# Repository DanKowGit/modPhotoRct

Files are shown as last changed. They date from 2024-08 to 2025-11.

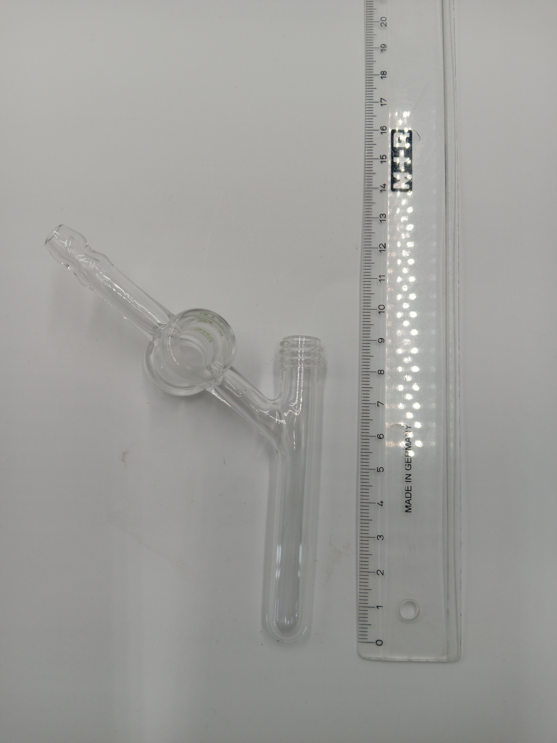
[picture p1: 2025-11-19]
01_CAD/00_Corpus/03_Corpus_130x130x130mm_water_splitting_group_power_measurment/05_reactors/GL14 5 mL schlenk flask.jpg

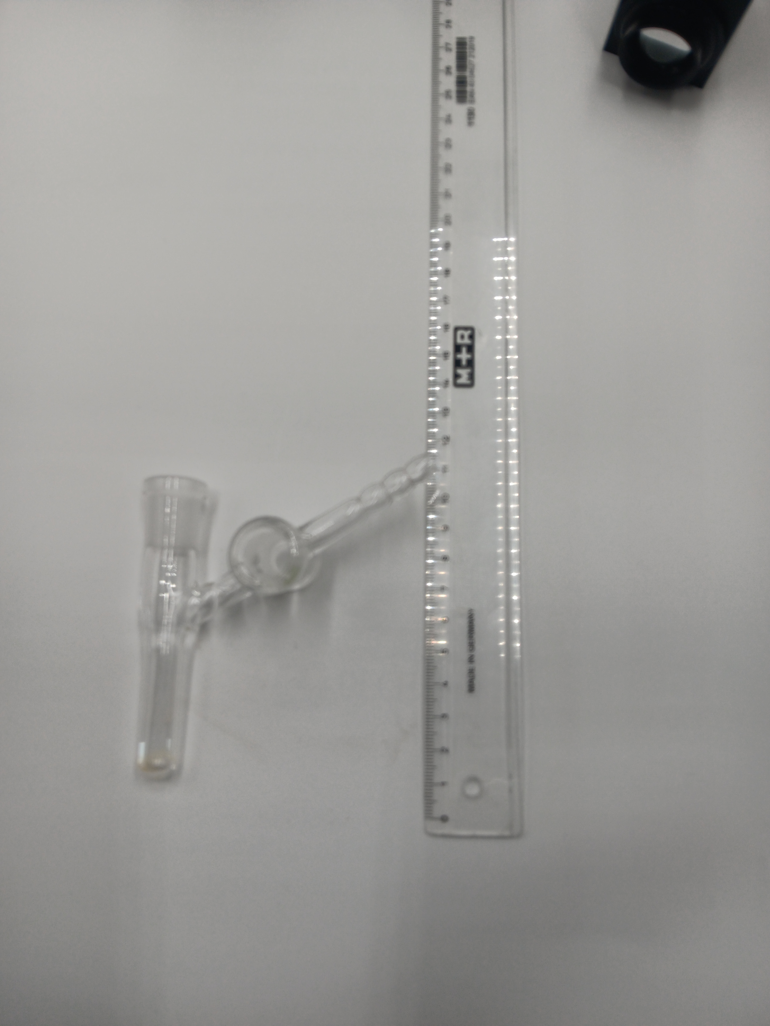
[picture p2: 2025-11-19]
01_CAD/00_Corpus/03_Corpus_130x130x130mm_water_splitting_group_power_measurment/05_reactors/NS14 5 mL schlenk flask.jpg

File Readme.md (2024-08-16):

# modularPhotoreactor

A modular and characterized open source photoreactor and the mutli-batch screening phototreactor extension

## Documentation

The assembly of the devices is documented in the [CAD section](./01_CAD/).

See also the 3D-pdfs for detailed assembly instructions in the [assembly section](./03_ASSEMBLY_INSTRUCTIONS/).

The Python modules for the operation of the reactor controller are documented in the repository [Py4ModPhotoreactor](https://github.com/photonZfeed/Py4ModPhotoreactor). See also the fairly detailed docstrings in the code. 

## Folder Structure

```
📦modPhotoRct
┣ 📂01_CAD
┃   ┣ 📂00_Corpus
┃   ┃   ┣ 📂00_Corpus_90x90x100mm
┃   ┃   ┃   ┣ 📂00_corpus
┃   ┃   ┃   ┃   ┣ 📜corpus_90x90x100mm_back_wall.stl
┃   ┃   ┃   ┃   ┣ 📜corpus_90x90x100mm_front_wall.stl
┃   ┃   ┃   ┃   ┣ 📜corpus_90x90x100mm_side_walls.stl
┃   ┃   ┃   ┃   ┣ 📜corpus_90x90x100mm_side_walls_LED_holder.stl
┃   ┃   ┃   ┃   ┣ 📜corpus_cover.stl
┃   ┃   ┃   ┃   ┗ 📜corpus_stand.stl
┃   ┃   ┃   ┣ 📂01_irradiation_module
┃   ┃   ┃   ┃   ┣ 📜20210104_Thorlabsl_modul.stl
┃   ┃   ┃   ┃   ┣ 📜corpus_90x90mm_irrad_Max350.stl
┃   ┃   ┃   ┃   ┣ 📜corpus_90x90mm_irrad_Max350_adapter.stl
┃   ┃   ┃   ┃   ┣ 📜corpus_90x90mm_irrad_Thorlabs.stl
┃   ┃   ┃   ┃   ┣ 📜corpus_90x90mm_irrad_Thorlabs_adapter.stl
┃   ┃   ┃   ┃   ┣ 📜corpus_90x90mm_irrad_Thorlabs_collimator.stl
┃   ┃   ┃   ┃   ┗ 📜corpus_90x90mm_irrad_starcool.stl
┃   ┃   ┃   ┣ 📂02_stirring_module
┃   ┃   ┃   ┃   ┣ 📜corpus_90x90mm_stirring_module.stl
┃   ┃   ┃   ┃   ┣ 📜corpus_90x90mm_stirring_module_holder_electric_motor.stl
┃   ┃   ┃   ┃   ┣ 📜corpus_90x90mm_stirring_module_magnet_holder.stl
┃   ┃   ┃   ┃   ┗ 📜corpus_90x90mm_stirring_module_magnet_holder_blind_plug.stl
┃   ┃   ┃   ┗ 📂03_sample_holders
┃   ┃   ┃   ┃   ┣ 📜corpus_90x90mm_4mL_GCvial_ND13_10S_alignment_holder.stl
┃   ┃   ┃   ┃   ┣ 📜corpus_90x90mm_4mL_GCvial_ND13_10S_holder.stl
┃   ┃   ┃   ┃   ┣ 📜corpus_90x90mm_4mL_GCvial_ND13_1S_alignment_holder.stl
┃   ┃   ┃   ┃   ┣ 📜corpus_90x90mm_4mL_GCvial_ND13_1S_holder.stl
┃   ┃   ┃   ┃   ┣ 📜corpus_90x90mm_4mL_GCvial_ND13_4S_alignment_holder.stl
┃   ┃   ┃   ┃   ┣ 📜corpus_90x90mm_4mL_GCvial_ND13_4S_holder.stl
┃   ┃   ┃   ┃   ┣ 📜corpus_90x90mm_4mL_GCvial_ND13_6S_alignment_holder.stl
┃   ┃   ┃   ┃   ┣ 📜corpus_90x90mm_4mL_GCvial_ND13_6S_holder.stl
┃   ┃   ┃   ┃   ┣ 📜corpus_90x90mm_4mL_GCvial_ND13_8S_alignment_holder.stl
┃   ┃   ┃   ┃   ┣ 📜corpus_90x90mm_4mL_GCvial_ND13_8S_holder.stl
┃   ┃   ┃   ┃   ┣ 📜corpus_90x90mm_8mL_GCvial_ND13_10S_alignment_holder.stl
┃   ┃   ┃   ┃   ┗ 📜corpus_90x90mm_8mL_GCvial_ND13_1S_alignment_holder.stl
┃   ┃   ┣ 📂01_Corpus_90x90x140mm
┃   ┃   ┃   ┣ 📂00_corpus
┃   ┃   ┃   ┃   ┣ 📜corpus_90x90x140mm_back_wall.stl
┃   ┃   ┃   ┃   ┣ 📜corpus_90x90x140mm_front_wall.stl
┃   ┃   ┃   ┃   ┣ 📜corpus_90x90x140mm_side_walls.stl
┃   ┃   ┃   ┃   ┣ 📜corpus_90x90x140mm_side_walls_LED_Irradiation_Firesting_ports.ipt
┃   ┃   ┃   ┃   ┣ 📜corpus_90x90x140mm_side_walls_LED_Irradiation_Firesting_ports.stl
┃   ┃   ┃   ┃   ┣ 📜corpus_90x90x140mm_side_walls_LED_Irradiation_Firesting_ports.yaml
┃   ┃   ┃   ┃   ┣ 📜corpus_cover.stl
┃   ┃   ┃   ┃   ┗ 📜corpus_stand.stl
┃   ┃   ┃   ┣ 📂01_irradiation_module
┃   ┃   ┃   ┃   ┣ 📜20210104_Thorlabsl_modul.stl
┃   ┃   ┃   ┃   ┣ 📜corpus_90x90mm_irrad_Max350.stl
┃   ┃   ┃   ┃   ┣ 📜corpus_90x90mm_irrad_Max350_adapter.stl
┃   ┃   ┃   ┃   ┣ 📜corpus_90x90mm_irrad_Thorlabs.stl
┃   ┃   ┃   ┃   ┣ 📜corpus_90x90mm_irrad_Thorlabs_adapter.stl
┃   ┃   ┃   ┃   ┣ 📜corpus_90x90mm_irrad_Thorlabs_collimator.stl
┃   ┃   ┃   ┃   ┗ 📜corpus_90x90mm_irrad_starcool.stl
┃   ┃   ┃   ┣ 📂02_stirring_module
┃   ┃   ┃   ┃   ┣ 📜corpus_90x90mm_stirring_module.stl
┃   ┃   ┃   ┃   ┣ 📜corpus_90x90mm_stirring_module_holder_electric_motor.stl
┃   ┃   ┃   ┃   ┣ 📜corpus_90x90mm_stirring_module_magnet_holder.stl
┃   ┃   ┃   ┃   ┗ 📜corpus_90x90mm_stirring_module_magnet_holder_blind_plug.stl
┃   ┃   ┃   ┗ 📂03_sample_holders
┃   ┃   ┃   ┃   ┣ 📜corpus_90x90mm_4mL_GCvial_ND13_10S_alignment_holder.stl
┃   ┃   ┃   ┃   ┣ 📜corpus_90x90mm_4mL_GCvial_ND13_10S_holder.stl
┃   ┃   ┃   ┃   ┣ 📜corpus_90x90mm_4mL_GCvial_ND13_1S_alignment_holder.stl
┃   ┃   ┃   ┃   ┣ 📜corpus_90x90mm_4mL_GCvial_ND13_1S_holder.stl
┃   ┃   ┃   ┃   ┣ 📜corpus_90x90mm_4mL_GCvial_ND13_4S_alignment_holder.stl
┃   ┃   ┃   ┃   ┣ 📜corpus_90x90mm_4mL_GCvial_ND13_4S_holder.stl
┃   ┃   ┃   ┃   ┣ 📜corpus_90x90mm_4mL_GCvial_ND13_6S_alignment_holder.stl
┃   ┃   ┃   ┃   ┣ 📜corpus_90x90mm_4mL_GCvial_ND13_6S_holder.stl
┃   ┃   ┃   ┃   ┣ 📜corpus_90x90mm_4mL_GCvial_ND13_8S_alignment_holder.stl
┃   ┃   ┃   ┃   ┣ 📜corpus_90x90mm_4mL_GCvial_ND13_8S_holder.stl
┃   ┃   ┃   ┃   ┣ 📜corpus_90x90mm_8mL_GCvial_ND13_10S_alignment_holder.stl
┃   ┃   ┃   ┃   ┗ 📜corpus_90x90mm_8mL_GCvial_ND13_1S_alignment_holder.stl
┃   ┃   ┗ 📂02_Corpus_130x130x130mm
┃   ┃   ┃   ┣ 📂00_corpus
┃   ┃   ┃   ┃   ┣ 📜corpus130x130mm_side_walls.stl
┃   ┃   ┃   ┃   ┣ 📜corpus_130x130mm_back_wall.stl
┃   ┃   ┃   ┃   ┣ 📜corpus_130x130mm_cover.stl
┃   ┃   ┃   ┃   ┣ 📜corpus_130x130mm_front_wall_monting_thermal_hose.stl
┃   ┃   ┃   ┃   ┣ 📜corpus_130x130mm_side_wall_left.stl
┃   ┃   ┃   ┃   ┣ 📜corpus_130x130mm_side_wall_right.stl
┃   ┃   ┃   ┃   ┣ 📜corpus_130x130mm_stand_20mm.stl
┃   ┃   ┃   ┃   ┣ 📜fin_back_wall.stl
┃   ┃   ┃   ┃   ┣ 📜fin_front_wall.stl
┃   ┃   ┃   ┃   ┣ 📜spacer_side_walls_5mm.stl
┃   ┃   ┃   ┃   ┗ 📜spacer_stand_5mm.stl
┃   ┃   ┃   ┣ 📂01_irradiation_module
┃   ┃   ┃   ┃   ┗ 📜irrad_module.stl
┃   ┃   ┃   ┣ 📂02_sample_holders
┃   ┃   ┃   ┃   ┣ 📜corpus_130x130mm_GCvial_ND13_18S_alignment_holder.stl
┃   ┃   ┃   ┃   ┣ 📜corpus_130x130mm_GCvial_ND13_18S_holder.stl
┃   ┃   ┃   ┃   ┣ 📜corpus_130x130mm_GCvial_ND13_1S_alignment_holder.stl
┃   ┃   ┃   ┃   ┗ 📜corpus_130x130mm_GCvial_ND13_1S_holder.stl
┃   ┃   ┃   ┗ 📂03_tempering_module
┃   ┃   ┃   ┃   ┣ 📜back_mounting_thermo_hose.stl
┃   ┃   ┃   ┃   ┣ 📜fan_holder.stl
┃   ┃   ┃   ┃   ┣ 📜holder_tempering_module.stl
┃   ┃   ┃   ┃   ┣ 📜mounting_alu_water_cooler.stl
┃   ┃   ┃   ┃   ┗ 📜spacer_holder_tempering_module.stl
┃   ┣ 📂01_controller
┃   ┃   ┣ 📜controller_case.stl
┃   ┃   ┣ 📜controller_case_LCD_holder.stl
┃   ┃   ┗ 📜controller_electronic_board_holder.stl
┃   ┣ 📂02_Peripheral_Modules
┃   ┃   ┣ 📂00_ambient_temperature
┃   ┃   ┃   ┣ 📜base_plate_ambient_temperature_extension.stl
┃   ┃   ┃   ┗ 📜case_ambient_temperature_extension.stl
┃   ┃   ┣ 📂01_tempering_extension
┃   ┃   ┃   ┣ 📜base_plate.stl
┃   ┃   ┃   ┗ 📜case_tempering_extension.stl
┃   ┃   ┣ 📂02_master_extension
┃   ┃   ┃   ┣ 📜base_plate.stl
┃   ┃   ┃   ┗ 📜case_master_extension.stl
┃   ┃   ┣ 📂03_membrane_pump_extension
┃   ┃   ┃   ┣ 📜base_plate_membrane_pump.stl
┃   ┃   ┃   ┣ 📜base_plate_membrane_pump_exension.stl
┃   ┃   ┃   ┣ 📜case_membrane_pump.stl
┃   ┃   ┃   ┗ 📜case_membrane_pump_extension.stl
┃   ┃   ┗ 📂04_pressure_sensor_extension
┃   ┃   ┃   ┣ 📜base_plate.stl
┃   ┃   ┃   ┣ 📜base_plate_updated.stl
┃   ┃   ┃   ┣ 📜case_pressure_extension.stl
┃   ┃   ┃   ┗ 📜case_pressure_extension_updated.stl
┃   ┗ 📂03_Multi_Batch_Screening_Photoreactor
┃   ┃   ┣ 📂00_Base_Module
┃   ┃   ┃   ┗ 📜Base_Module.stl
┃   ┃   ┣ 📂01_Irradiation_Module
┃   ┃   ┃   ┣ 📜300mm_alu_heatsink.stl
┃   ┃   ┃   ┣ 📜heatsink_holder_left.stl
┃   ┃   ┃   ┣ 📜heatsink_holder_right.stl
┃   ┃   ┃   ┗ 📜stand_irradiation_module.stl
┃   ┃   ┣ 📂02_Reflector_Module
┃   ┃   ┃   ┣ 📜PTFE_Side_Wall.stl
┃   ┃   ┃   ┣ 📜Reflector_Holder_Nut.stl
┃   ┃   ┃   ┗ 📜Reflector_Holder_Screw.stl
┃   ┃   ┣ 📂03_Mobile_Cover
┃   ┃   ┃   ┣ 📜back.stl
┃   ┃   ┃   ┣ 📜connector.stl
┃   ┃   ┃   ┣ 📜front.stl
┃   ┃   ┃   ┣ 📜sides.stl
┃   ┃   ┃   ┗ 📜top.stl
┃   ┃   ┗ 📂04_Accesories
┃   ┃   ┃   ┗ 📂00_UV_Vis_Cell_4mL_GC_Vial
┃   ┃   ┃   ┃   ┣ 📜UV_vis_cell_4mL_GC_vial_SLA.png
┃   ┃   ┃   ┃   ┗ 📜UV_vis_cell_4mL_GC_vial_SLA.stl
┣ 📂02_MATERIALS
┃   ┣ 📂00_electronics
┃   ┃   ┣ 📂00_Tinkerforge
┃   ┃   ┃   ┗ 📜Tinkerforge.txt
┃   ┃   ┣ 📂01_LEDs
┃   ┃   ┃   ┣ 📂RGBA
┃   ┃   ┃   ┃   ┗ 📜LZ4-20MA00-0000.txt
┃   ┃   ┃   ┣ 📂UV
┃   ┃   ┃   ┃   ┣ 📂365nm
┃   ┃   ┃   ┃   ┃   ┗ 📜LST1-01G01-UV01-00.txt
┃   ┃   ┃   ┃   ┣ 📂385nm
┃   ┃   ┃   ┃   ┃   ┗ 📜LZ1-10UB00-01U4.txt
┃   ┃   ┃   ┃   ┗ 📂405nm
┃   ┃   ┃   ┃   ┃   ┣ 📂onecore
┃   ┃   ┃   ┃   ┃   ┃   ┗ 📜LZ1-10UB00-01U7.txt
┃   ┃   ┃   ┃   ┃   ┗ 📂quadcore
┃   ┃   ┃   ┃   ┃   ┃   ┗ 📜LZ4-V0UB0R-00U8.txt
┃   ┃   ┃   ┣ 📂blue
┃   ┃   ┃   ┃   ┣ 📂453nm
┃   ┃   ┃   ┃   ┃   ┗ 📜LZ4-00B208-0000.txt
┃   ┃   ┃   ┃   ┣ 📂455nm
┃   ┃   ┃   ┃   ┃   ┗ 📜LST1-01F06-RYL1-00.txt
┃   ┃   ┃   ┃   ┗ 📂460nm
┃   ┃   ┃   ┃   ┃   ┣ 📜5412869-LED_2520Engin_Datasheet_LuxiGen_LZ1-00DB00-1532005.pdf
┃   ┃   ┃   ┃   ┃   ┗ 📜LZ1-00DB00.txt
┃   ┃   ┃   ┗ 📂green
┃   ┃   ┃   ┃   ┗ 📂530nm
┃   ┃   ┃   ┃   ┃   ┗ 📜LST1-01F06-GRN1-00.txt
┃   ┃   ┣ 📂02_raspberry_pi
┃   ┃   ┃   ┗ 📜raspberry_pi_4_8GB.txt
┃   ┃   ┣ 📂03_sd_card
┃   ┃   ┃   ┗ 📜SD_card.txt
┃   ┃   ┣ 📂04_peltier_element
┃   ┃   ┃   ┗ 📜peltier.txt
┃   ┃   ┣ 📂05_power_supplies
┃   ┃   ┃   ┣ 📂00_12V_5A
┃   ┃   ┃   ┃   ┗ 📜12V_5A.txt
┃   ┃   ┃   ┣ 📂01_24V_6A
┃   ┃   ┃   ┃   ┗ 📜24V_6A.txt
┃   ┃   ┃   ┗ 📂02_Analoge_ACDC_Laboratory_Power_Supply
┃   ┃   ┃   ┃   ┗ 📜KORAD_KA3005P.txt
┃   ┃   ┣ 📂06_small_parts
┃   ┃   ┃   ┣ 📂00_stripboard
┃   ┃   ┃   ┃   ┗ 📜stripboard_WR_914-HP.txt
┃   ┃   ┃   ┣ 📂01_connection_jacks
┃   ┃   ┃   ┃   ┣ 📜2Pin_PCB_Mount_2.5mm_Pitch.txt
┃   ┃   ┃   ┃   ┣ 📜2Pin_PCB_Mount_5mm_Pitch.txt
┃   ┃   ┃   ┃   ┣ 📜Cable_extension_PWM_4-Pin_Moltex.txt
┃   ┃   ┃   ┃   ┣ 📜DC_Jack.txt
┃   ┃   ┃   ┃   ┣ 📜banana_plug_female.txt
┃   ┃   ┃   ┃   ┣ 📜banana_plug_male.txt
┃   ┃   ┃   ┃   ┗ 📜wago_2Conductur_clamp.txt
┃   ┃   ┃   ┣ 📂02_Stacking_Header_Raspberry_Pi
┃   ┃   ┃   ┃   ┗ 📜Stacking_Header_Raspberry_Pi.txt
┃   ┃   ┃   ┣ 📂03_two_position_switch
┃   ┃   ┃   ┃   ┗ 📜two_position_switch.txt
┃   ┃   ┃   ┗ 📂04_silicone_wire
┃   ┃   ┃   ┃   ┗ 📜silicone_wire.txt
┃   ┃   ┣ 📂07_LED_drivers
┃   ┃   ┃   ┣ 📜350mA_driver.txt
┃   ┃   ┃   ┣ 📜500mA_driver.txt
┃   ┃   ┃   ┗ 📜700mA_driver.txt
┃   ┃   ┣ 📂08_membrane_pump
┃   ┃   ┃   ┣ 📜Membrane_Pump.txt
┃   ┃   ┃   ┗ 📜accessories_membrane_pump.txt
┃   ┃   ┗ 📂09_fans
┃   ┃   ┃   ┣ 📂00_fan_corpus_90x90mm
┃   ┃   ┃   ┃   ┗ 📜fan.txt
┃   ┃   ┃   ┣ 📂01_fan_corpus_130x130mm
┃   ┃   ┃   ┃   ┣ 📜fan.txt
┃   ┃   ┃   ┃   ┗ 📜fan_update.txt
┃   ┃   ┃   ┣ 📂02_power_supply_fan_corpus_90x90mm
┃   ┃   ┃   ┃   ┗ 📜power_supply.txt
┃   ┃   ┃   ┗ 📂03_Pi_Fan
┃   ┃   ┃   ┃   ┗ 📜Pi_Fan.txt
┃   ┗ 📂01_accessories
┃   ┃   ┣ 📂00_thermal_tube
┃   ┃   ┃   ┗ 📜thermal_hose.txt
┃   ┃   ┣ 📂01_hose_clamps
┃   ┃   ┃   ┗ 📜hose_clamp.txt
┃   ┃   ┣ 📂02_screws_nuts
┃   ┃   ┃   ┣ 📂00_M3_Set
┃   ┃   ┃   ┃   ┗ 📜M3_screw_set.txt
┃   ┃   ┃   ┣ 📂01_Nylon_Spacer
┃   ┃   ┃   ┃   ┗ 📜nylon_spacer.txt
┃   ┃   ┃   ┗ 📂02_M3_60mm
┃   ┃   ┃   ┃   ┗ 📜M3_60mm.txt
┃   ┃   ┣ 📂03_cooler
┃   ┃   ┃   ┣ 📂00_tempering_module_cooler
┃   ┃   ┃   ┃   ┣ 📂00_pelltier_cooler
┃   ┃   ┃   ┃   ┃   ┗ 📜Alpine AM4 Passive.txt
┃   ┃   ┃   ┃   ┗ 📂01_alu_water_cooler
┃   ┃   ┃   ┃   ┃   ┗ 📜alu_water_cooler.txt
┃   ┃   ┃   ┗ 📂01_LED_cooler
┃   ┃   ┃   ┃   ┣ 📂00_25mm_cooler
┃   ┃   ┃   ┃   ┃   ┗ 📜sink_s-1265491.txt
┃   ┃   ┃   ┃   ┣ 📂01_50mm_cooler
┃   ┃   ┃   ┃   ┃   ┗ 📜sink_s-1265491.txt
┃   ┃   ┃   ┃   ┗ 📂02_300mm_cooler
┃   ┃   ┃   ┃   ┃   ┗ 📜ATS-EXL75-300-R0.txt
┃   ┃   ┣ 📂04_foam_rubber_seal
┃   ┃   ┃   ┗ 📜foam_rubber_seal.txt
┃   ┃   ┗ 📂05_PTFE
┃   ┃   ┃   ┣ 📂00_technical_PTFE
┃   ┃   ┃   ┃   ┗ 📜technical_PTFE.txt
┃   ┃   ┃   ┗ 📂01_optical_PTFE
┃   ┃   ┃   ┃   ┗ 📜optical_PTFE.txt
┣ 📂03_ASSEMBLY_INSTRUCTIONS
┃   ┣ 📂00_Corpus
┃   ┃   ┣ 📜Assembly_Photoreactor_Corpus_130x130x130mm.pdf
┃   ┃   ┣ 📜Assembly_Photoreactor_Corpus_90x90x140mm.pdf
┃   ┃   ┗ 📜Assembly_Photoreactor_Corpus_90x90x90mm.pdf
┃   ┣ 📂01_Controller
┃   ┃   ┣ 📜20211029_Stripboard_drill_holes.pdf
┃   ┃   ┣ 📜Controller_Documentation.pdf
┃   ┃   ┣ 📜Controller_circuit_diagram.pdf
┃   ┃   ┣ 📜Controller_circuit_diagram.svg
┃   ┃   ┣ 📜Logic_Controller.pdf
┃   ┃   ┣ 📜Logic_Controller.svg
┃   ┃   ┗ 📜Logic_Controller.vsdx
┃   ┣ 📂02_Peripheral_Modules
┃   ┃   ┣ 📂00_Tempering_Module
┃   ┃   ┃   ┣ 📜Peltier_Circuit_Diagram.pdf
┃   ┃   ┃   ┗ 📜Peltier_Circuit_Diagram.svg
┃   ┃   ┗ 📂01_LED_Driver_Module
┃   ┃   ┃   ┗ 📜LED Driver Module.pdf
┃   ┣ 📂03_Irradiation_Module
┃   ┃   ┗ 📜assembly_instruction_LED_cooler.pdf
┃   ┗ 📂04_Multi_Batch_Screening_Phororeactor
┃   ┃   ┣ 📂00_Photoreactor
┃   ┃   ┃   ┗ 📜Multi_Batch_Screening_Photoreactor_assembly.pdf
┃   ┃   ┗ 📂01_Mobile_Cover
┃   ┃   ┃   ┣ 📜Mobile_Cover_assembly.pdf
┃   ┃   ┃   ┗ 📜Mobile_Cover_assembly.stl
┣ 📂04_IMAGES
┃   ┣ 📜Licenses.png
┃   ┗ 📜Licenses.svg
┣ 📜License.md
┗ 📜Readme.md
```

## More Information

<!--- Cite this repository: [![DOI](https://zenodo.org/badge/368164449.svg)](https://zenodo.org/badge/latestdoi/368164449) --->

## Publications

* [Making Photocatalysis Comparable Using a Modular and Characterized Open-Source Photoreactor](https://chemistry-europe.onlinelibrary.wiley.com/doi/full/10.1002/cptc.202200044)

* [Making Photocatalysts Screenable - A Milli Scale Multi-Batch Screening Photoreactor as Extension for the Modular Photoreactor](https://fill_in_the_blank)

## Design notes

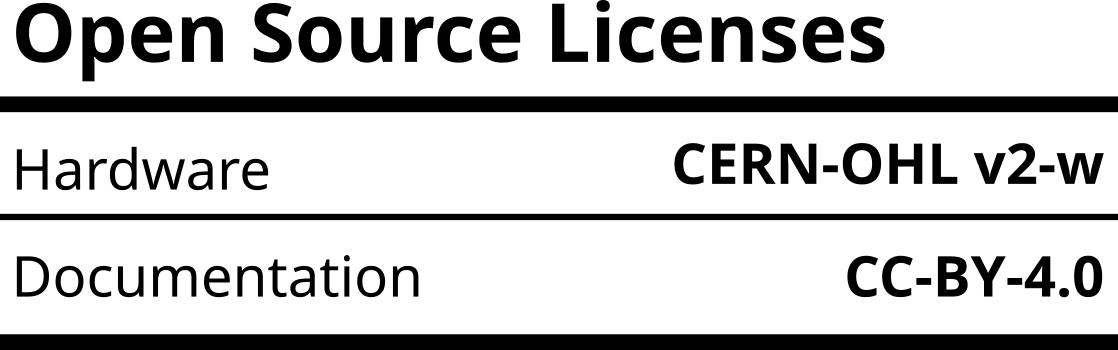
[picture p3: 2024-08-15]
04_IMAGES/Licenses.png

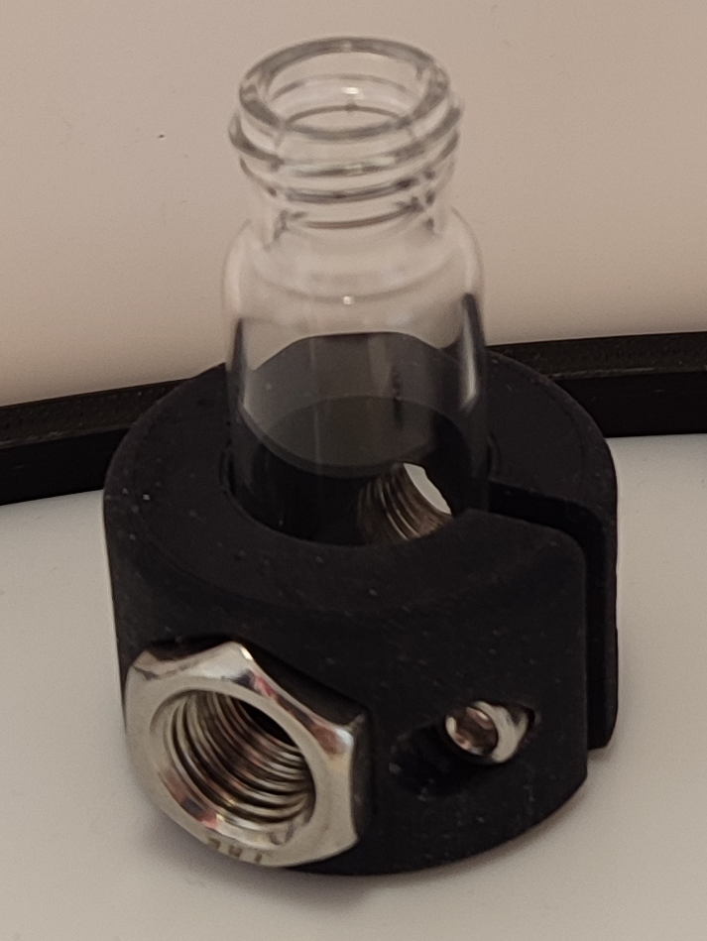
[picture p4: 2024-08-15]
01_CAD/03_Multi_Batch_Screening_Photoreactor/04_Accesories/00_UV_Vis_Cell_4mL_GC_Vial/UV_vis_cell_4mL_GC_vial_SLA.png

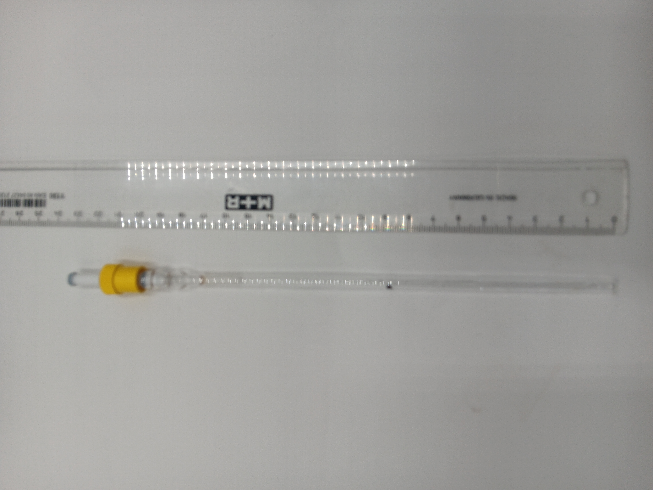
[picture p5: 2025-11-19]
01_CAD/00_Corpus/03_Corpus_130x130x130mm_water_splitting_group_power_measurment/05_reactors/Young type NMR tube.jpg

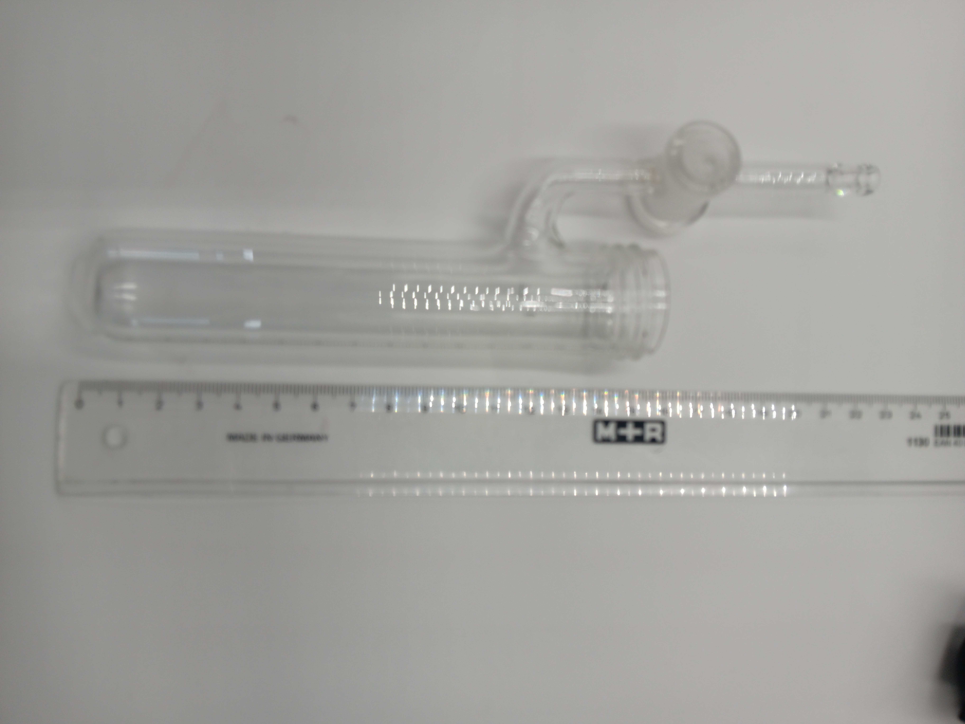
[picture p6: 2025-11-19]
01_CAD/00_Corpus/03_Corpus_130x130x130mm_water_splitting_group_power_measurment/05_reactors/GL25 50 mL schlenk flask.jpg

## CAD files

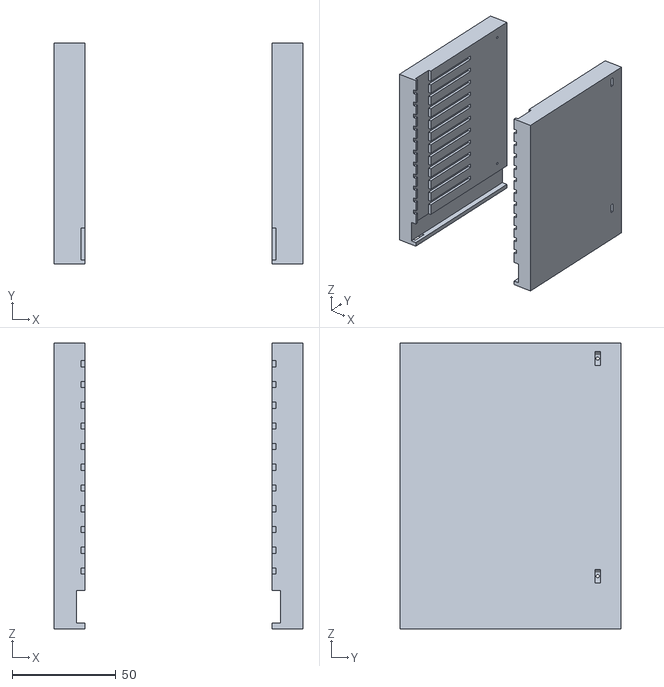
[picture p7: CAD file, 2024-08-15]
01_CAD/00_Corpus/00_Corpus_90x90x100mm/00_corpus/corpus_90x90x100mm_side_walls.stl
120.0 x 106.7 x 138.0

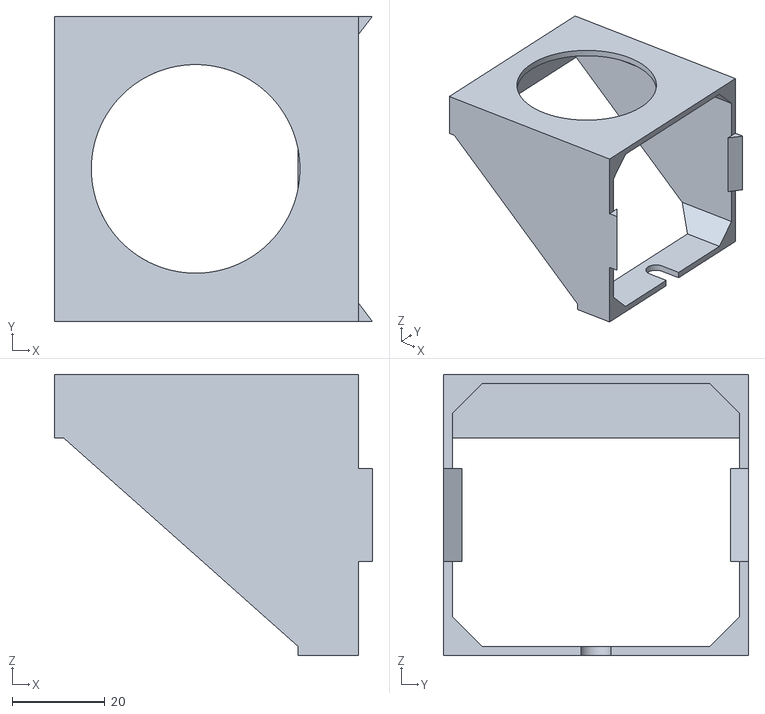
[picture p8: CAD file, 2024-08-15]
01_CAD/00_Corpus/00_Corpus_90x90x100mm/01_irradiation_module/corpus_90x90mm_irrad_Max350_adapter.stl
68.6 x 65.9 x 60.7

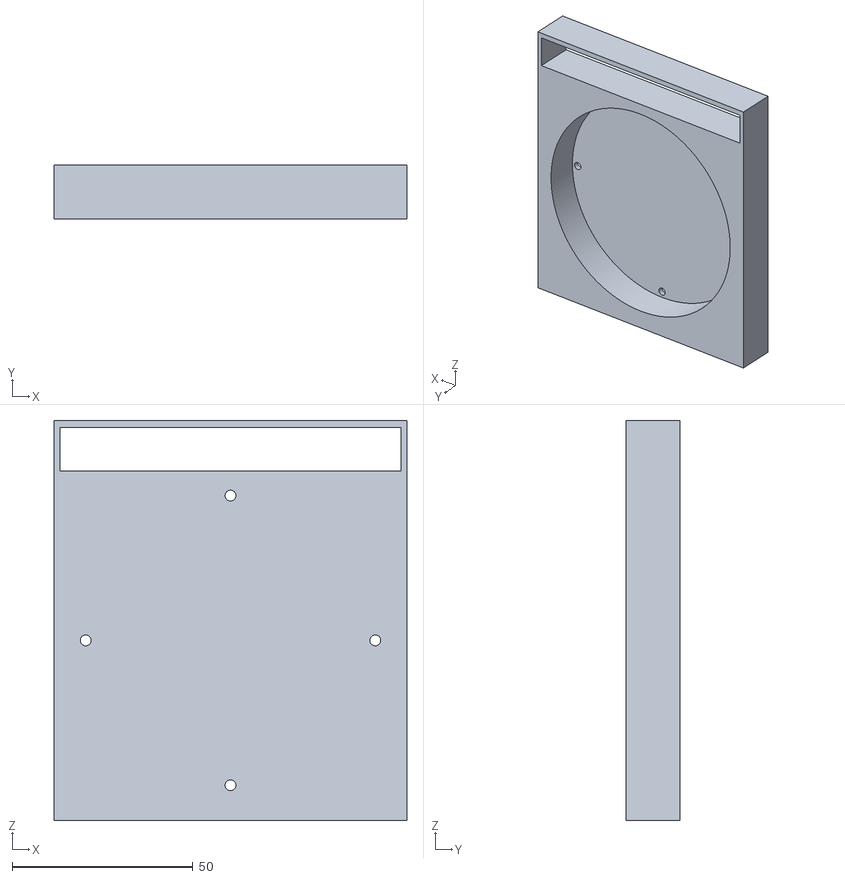
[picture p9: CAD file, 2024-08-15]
01_CAD/00_Corpus/00_Corpus_90x90x100mm/02_stirring_module/corpus_90x90mm_stirring_module.stl
97.5 x 15.0 x 110.5

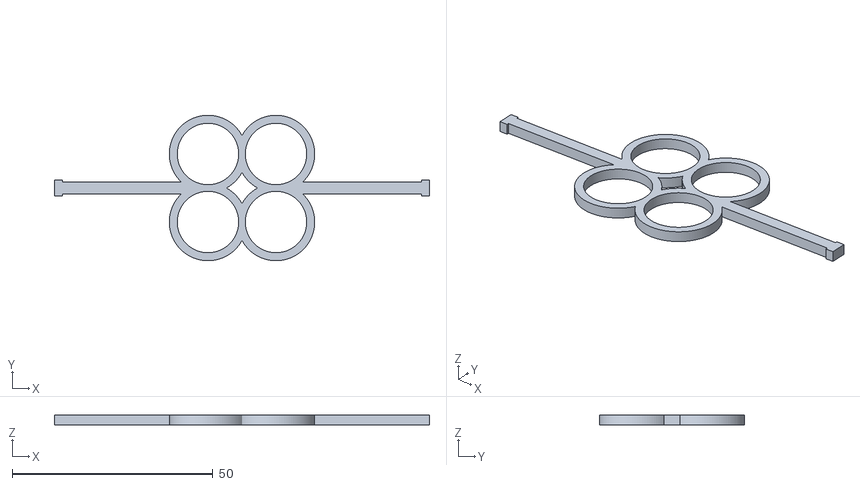
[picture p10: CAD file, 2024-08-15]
01_CAD/00_Corpus/00_Corpus_90x90x100mm/03_sample_holders/corpus_90x90mm_4mL_GCvial_ND13_4S_alignment_holder.stl
93.5 x 36.3 x 2.50

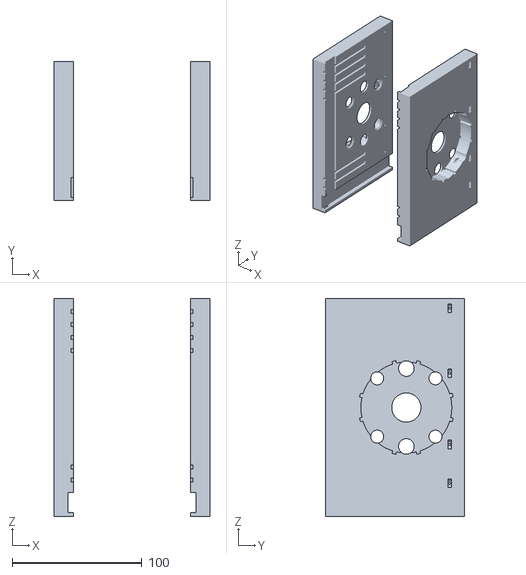
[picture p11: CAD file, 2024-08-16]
01_CAD/00_Corpus/01_Corpus_90x90x140mm/00_corpus/corpus_90x90x140mm_side_walls_LED_Irradiation_Firesting_ports.stl
120.0 x 106.7 x 168.0

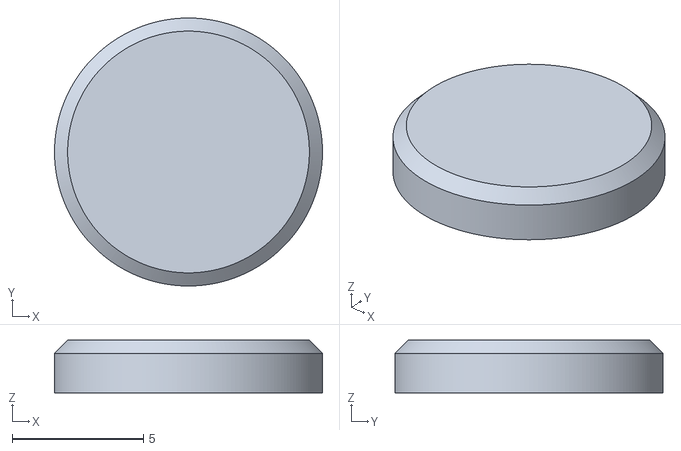
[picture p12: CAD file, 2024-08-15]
01_CAD/00_Corpus/01_Corpus_90x90x140mm/02_stirring_module/corpus_90x90mm_stirring_module_magnet_holder_blind_plug.stl
10.2 x 10.2 x 2.00

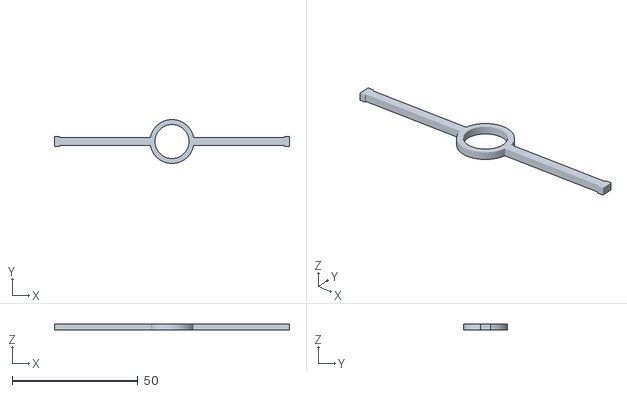
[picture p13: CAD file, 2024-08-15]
01_CAD/00_Corpus/01_Corpus_90x90x140mm/03_sample_holders/corpus_90x90mm_8mL_GCvial_ND13_1S_alignment_holder.stl
93.5 x 17.5 x 2.50

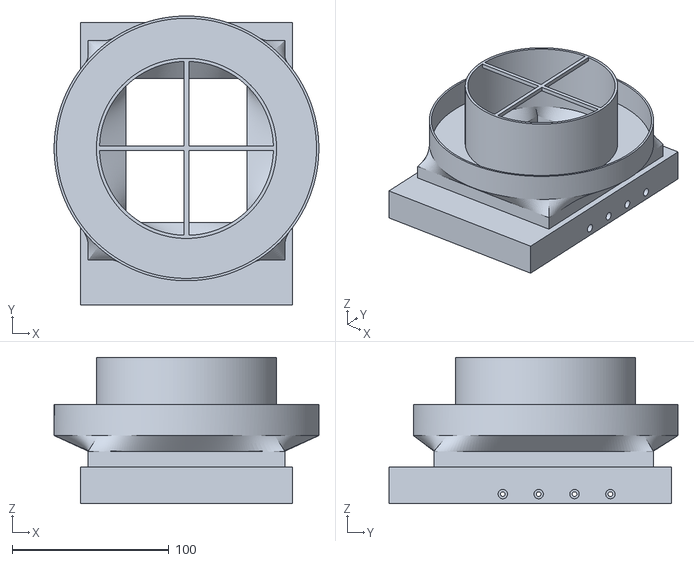
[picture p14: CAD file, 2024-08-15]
01_CAD/00_Corpus/02_Corpus_130x130x130mm/00_corpus/corpus_130x130mm_front_wall_monting_thermal_hose.stl
169.0 x 184.5 x 93.5

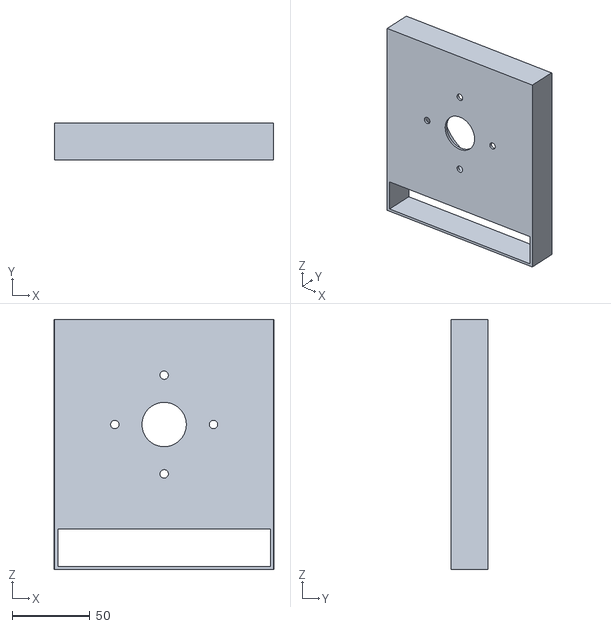
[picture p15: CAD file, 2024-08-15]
01_CAD/00_Corpus/02_Corpus_130x130x130mm/01_irradiation_module/irrad_module.stl
141.3 x 24.0 x 160.8

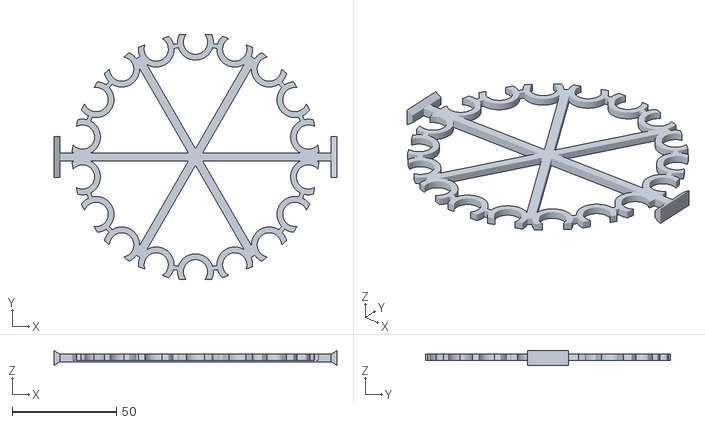
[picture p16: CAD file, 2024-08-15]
01_CAD/00_Corpus/02_Corpus_130x130x130mm/02_sample_holders/corpus_130x130mm_GCvial_ND13_18S_holder.stl
135.6 x 117.5 x 7.10

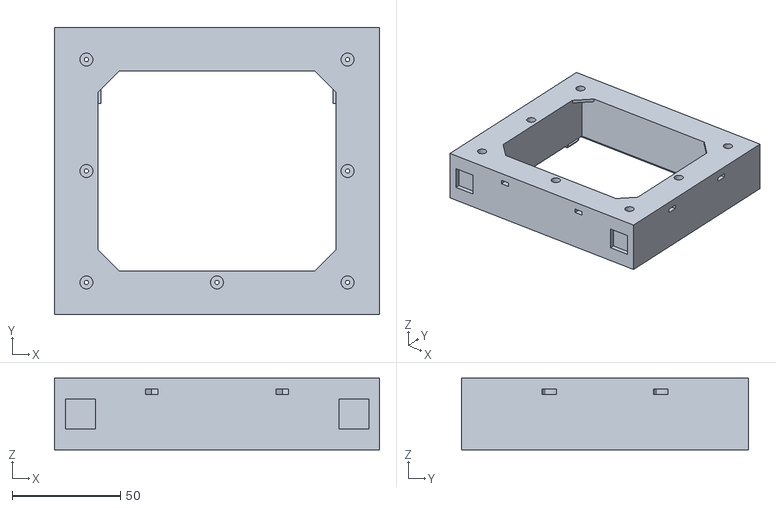
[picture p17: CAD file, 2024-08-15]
01_CAD/00_Corpus/02_Corpus_130x130x130mm/03_tempering_module/fan_holder.stl
150.2 x 132.5 x 33.1

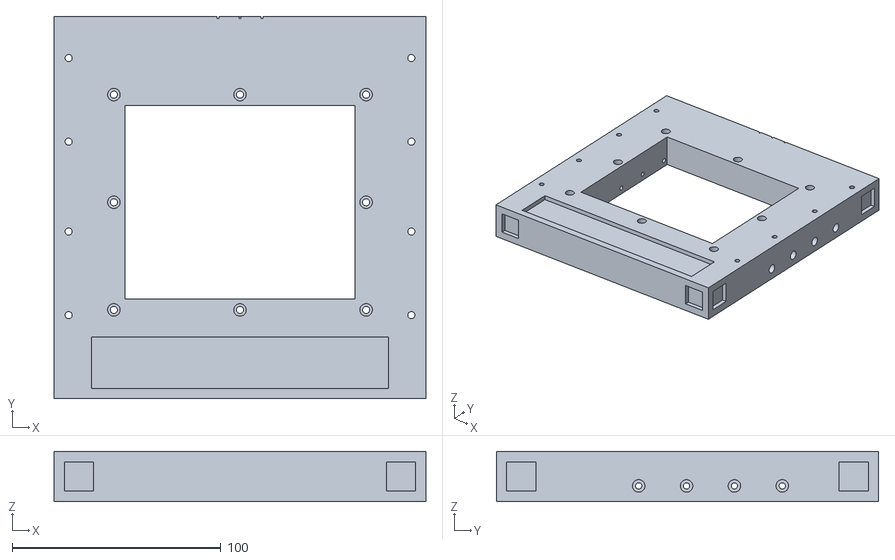
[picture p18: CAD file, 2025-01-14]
01_CAD/00_Corpus/03_Corpus_130x130x130mm_water_splitting_group/00_corpus/2024_08_21_Reaktorkorpus_modular_hinten.stl
178.0 x 183.0 x 24.0

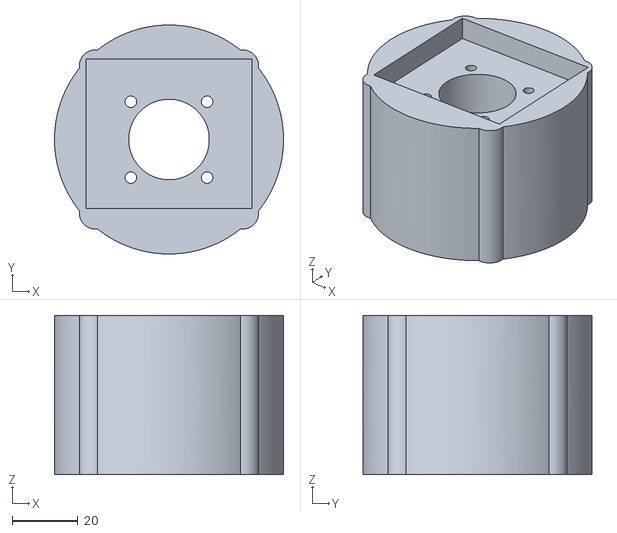
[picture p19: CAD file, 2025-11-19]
01_CAD/00_Corpus/03_Corpus_130x130x130mm_water_splitting_group/01_apertures/2024_09_13_beam_combiner_blende_UHP_LED.stl
69.6 x 69.6 x 48.3

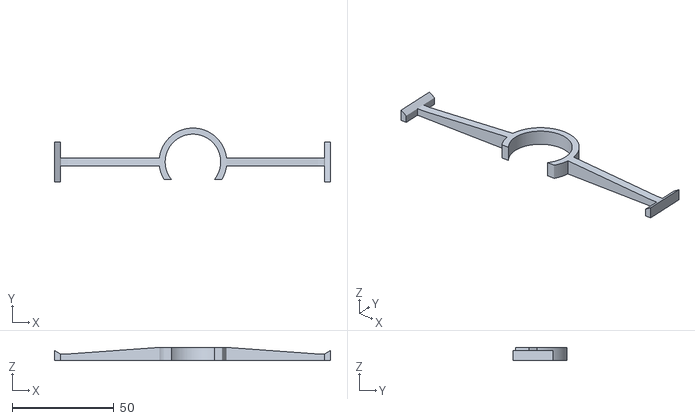
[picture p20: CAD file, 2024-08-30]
01_CAD/00_Corpus/03_Corpus_130x130x130mm_water_splitting_group/02_sample_holders/2024_08_28_Holer_GL25.stl
135.6 x 26.5 x 6.50

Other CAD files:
01_CAD/00_Corpus/03_Corpus_130x130x130mm_water_splitting_group_power_measurment/00_corpus/2025_01_29_Reaktorkorpus_hinten.stl
01_CAD/00_Corpus/03_Corpus_130x130x130mm_water_splitting_group_power_measurment/01_apertures/power_sensor_aperture_V1.1.stl
01_CAD/00_Corpus/03_Corpus_130x130x130mm_water_splitting_group_power_measurment/04_misc/2024_08_26_Fuss_5mm.stl
01_CAD/00_Corpus/00_Corpus_90x90x100mm/00_corpus/corpus_90x90x100mm_back_wall.stl
01_CAD/00_Corpus/00_Corpus_90x90x100mm/00_corpus/corpus_90x90x100mm_front_wall.stl
01_CAD/00_Corpus/00_Corpus_90x90x100mm/00_corpus/corpus_90x90x100mm_side_walls_LED_holder.stl
01_CAD/00_Corpus/00_Corpus_90x90x100mm/00_corpus/corpus_cover.stl
01_CAD/00_Corpus/00_Corpus_90x90x100mm/00_corpus/corpus_stand.stl
01_CAD/00_Corpus/00_Corpus_90x90x100mm/01_irradiation_module/20210104_Thorlabsl_modul.stl
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

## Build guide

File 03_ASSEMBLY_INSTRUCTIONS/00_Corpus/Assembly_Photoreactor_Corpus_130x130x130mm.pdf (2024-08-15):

setPageBoxes("Crop", 0, 0, [0,2000,2000,0]);

# Modular Photoreactor Assembly Instructions

TITLE | INSTRUCTIONS

Assembly of the Photoreactor Corpus 130x130x130mm

ORGANIZATION

Institute of Chemical
Engineering Ulm University
DESIGNER | Daniel Kowalczyk
1) LED Module assembly: slide the cooler with mounted LED into the 3D-printed holder. Fix the cooler with 4 M3 screws (length adjusted to the thickness of the cooler) and 4 M3 nuts as shown in the depiction of the setup.
2) Fixation of the ventilation fins: place the fins of the right length in the front and back part of the corpus fixed by each 8 M3 (length: 30 mm and 40 mm) screws.
3) Make sure to cut out foam sealings for every surface connecting the 3D-printed parts. This ensures sufficient tempering of the setup.
4) Corpus assembly: place 8 M3 nuts in the slits of the side parts of the corpus. Fix the back part of the corpus with 8 M3 (length: 30 mm) according to the graphical assembly instruction.
5) Assembly of the tempering module: The peltier elements must be connected in a row according to (A-B-C-D). Make sure to put heat conducting paste between all interfaces to assure sufficient heat conduction. Place the peltier elements A and B on top of the passive alumina cooler. Stack C and D on A and B according to the 3D graph. Make sure that each heating and cooling side of the Peltier elements face the same direction. Place the alumina water cooler on top of C and D. Cut a piece of the foam sealing to the dimensions of the water cooler (40x80mm) and place it on top of the cooler. Slide the whole tempering unit into the 3D-printed holder. Fix the alumina passive holder in place using the 3D-printed spacer. Fix the water cooler from the top using the four slotted screws delivered with the alumina passive cooler. Place the 15 M3 nuts into the slits of the 3D-printed holder. Fix the assembled tempering module with 8 M3 screws from the inside of the corpus (length: 30 mm).
6) Assembly of the fan module: fix the fan with four M3 screws (length: 30 mm) and four M3 nuts according to the 3D-graphic. Make sure the air flow is directed into the tempering module. Place 8 M3 nuts in the slits of the 3D-printed fan holder. Fix the fan module to the tempering module using 7 M3 screws (length: 30 mm).
7) Fixation of the tempering air inlet: fix the 3D-printed inlet using 8 M3 screws (length: 30 mm). Connect the tempering air inlet with the tempering air outlet using the thermoinsulated tubing with the hose clamps.

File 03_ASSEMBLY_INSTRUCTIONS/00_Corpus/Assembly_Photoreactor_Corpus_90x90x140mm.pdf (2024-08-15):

setPageBoxes("Crop", 0, 0, [0,2000,2000,0]);

# Modular Photoreactor Assembly Instructions

TITLE | INSTRUCTIONS

Assembly Instruction
Photoreactor Corpus
90x90x140mm

ORGANIZATION

Institute of Chemical
Engineering Ulm University
DESIGNER | Daniel Kowalczyk
1) LED Module assembly: slide the cooler with mounted LED into the 3D-printed holder. Fix the cooler with 4 M3 screws (length adjusted to the thickness of the cooler) and 4 M3 nuts as shown in the depiction of the setup.
2) Corpus assembly: place 6 M3 nuts in the slits of the side parts of the corpus. Fix the back part of the corpus with 4 M3 screws (length: 30 mm) according to the graphical assembly instruction. Fix the fan (120x120mm) to the back part of the corpus with 4 M3 screws (length: 70 mm) according to the graphical assembly instruction.

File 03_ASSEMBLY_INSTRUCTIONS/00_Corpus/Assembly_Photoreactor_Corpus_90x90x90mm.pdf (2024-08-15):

setPageBoxes("Crop", 0, 0, [0,2000,2000,0]);

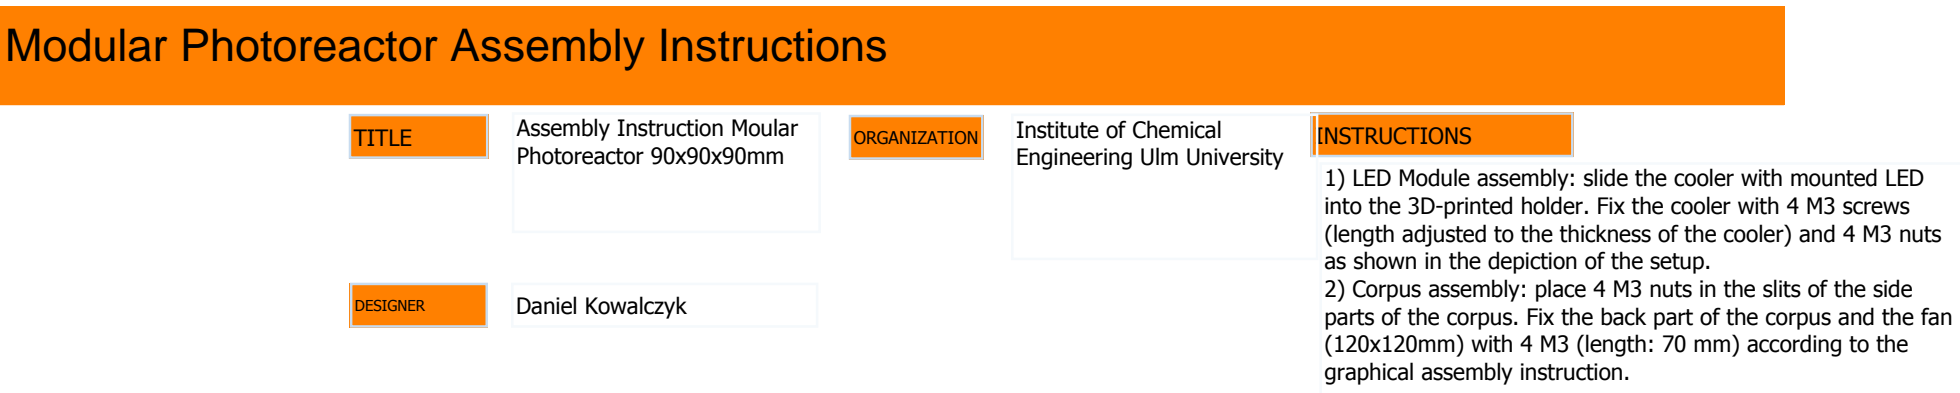
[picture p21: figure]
TITLE; INSTRUCTIONS; Assembly Instruction Moular Photoreactor 90x90x90mm; ORGANIZATION; Institute of Chemical Engineering Ulm University; DESIGNER; Daniel Kowalczyk; as shown in the depiction of the setup.; graphical assembly instruction.

# Modular Photoreactor Assembly Instructions

1) LED Module assembly: slide the cooler with mounted LED into the 3D-printed holder. Fix the cooler with 4 M3 screws (length adjusted to the thickness of the cooler) and 4 M3 nuts
2) Corpus assembly: place 4 M3 nuts in the slits of the side parts of the corpus. Fix the back part of the corpus and the fan (120x120mm) with 4 M3 (length: 70 mm) according to the

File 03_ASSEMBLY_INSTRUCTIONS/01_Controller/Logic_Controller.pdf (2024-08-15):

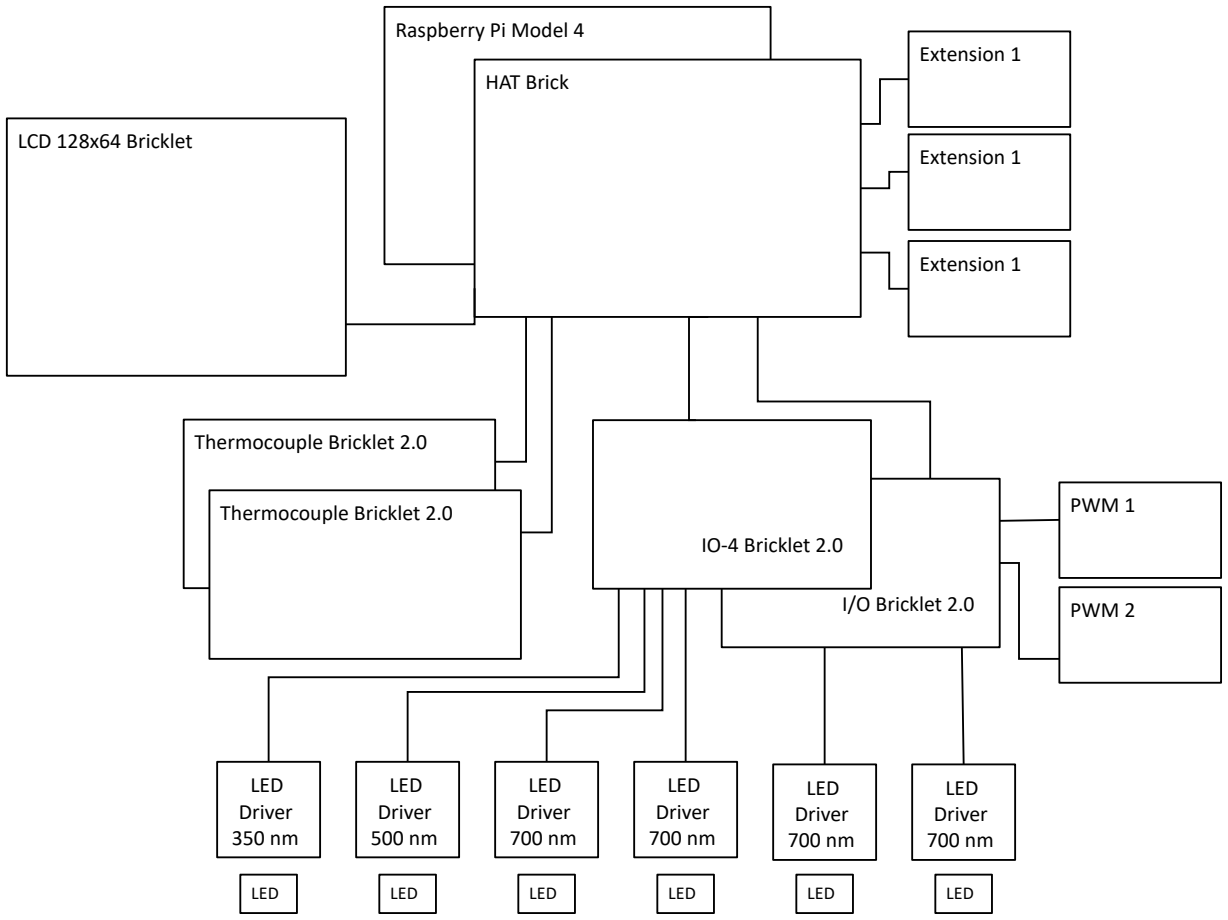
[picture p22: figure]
Raspberry Pi Model 4; HAT Brick; Thermocouple Bricklet 2.0; LED Driver 350 nm; LED; LED Driver 500 nm; LED Driver 700 nm; I/O Bricklet 2.0; IO-4 Bricklet 2.0; LCD 128x64 Bricklet; PWM 1; PWM 2; Extension 1

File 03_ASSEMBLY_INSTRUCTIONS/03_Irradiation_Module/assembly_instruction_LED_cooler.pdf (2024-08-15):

setPageBoxes("Crop", 0, 0, [0,2000,2000,0]);

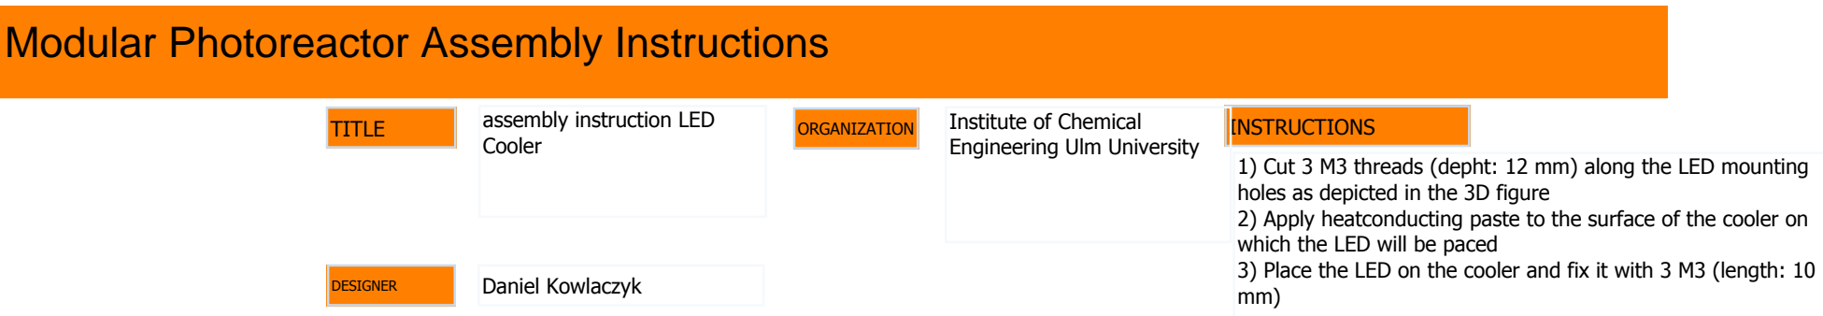
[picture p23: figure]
TITLE; INSTRUCTIONS; assembly instruction LED Cooler; ORGANIZATION; Institute of Chemical Engineering Ulm University; DESIGNER; Daniel Kowlaczyk; holes as depicted in the 3D figure; which the LED will be paced

# Modular Photoreactor Assembly Instructions

1) Cut 3 M3 threads (depht: 12 mm) along the LED mounting
2) Apply heatconducting paste to the surface of the cooler on
3) Place the LED on the cooler and fix it with 3 M3 (length: 10

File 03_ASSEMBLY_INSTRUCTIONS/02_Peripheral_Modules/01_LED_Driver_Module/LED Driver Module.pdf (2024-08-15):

## LED Driver Module

### Parts:

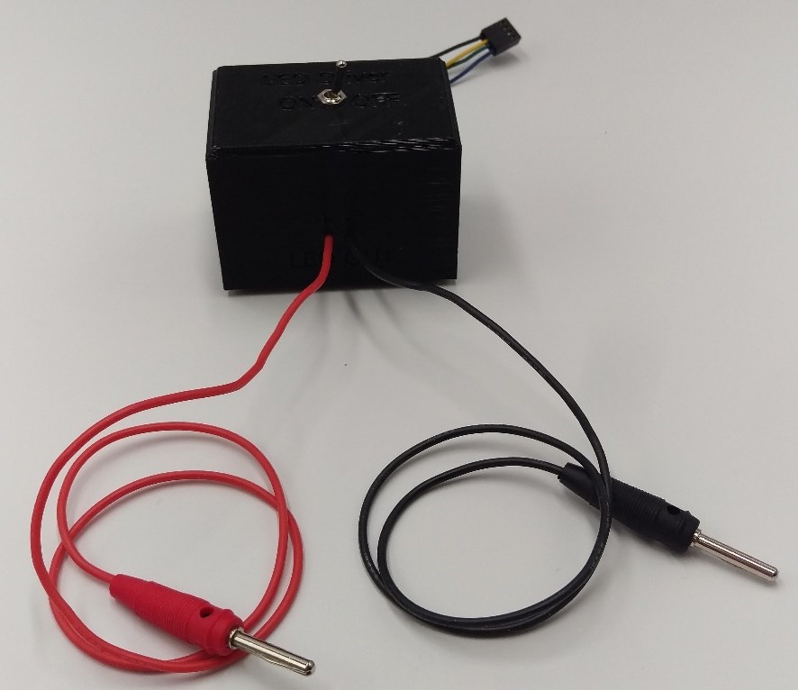
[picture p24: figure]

- LED Driver (LDD-L-SPEC-1291586)
- Two position switch
- Silicone wire
- Cable extension PWM 4-Pin Moltex
- Red banana plug
- black banana plug
- 3D printed LED diver case
- 3D printed base plate
- 3D printed LED driver holder
- 4 x 10 mm nylon spacer
- 4 x M3 nylon nuts
- 4 x M3 steel nuts
- 8 x M3 8 mm steel screws

### Assembly Instructions

1) Connect the banana plugs to the wires and place them inside of the holes (LED out) in the 3D printed case. Cut the Cable extension PWM 4-Pin Moltex cables approximately at half of their length. Take the female side of the Cable extension PWM 4-Pin Moltex and place the 4 Cables in the 4 holes of the 3D printed case.
2) Insert the two-position switch between the yellow wire of Cable extension PWM 4-Pin Moltex. Therefore, cut the yellow cable in half and put the switch in between. Connect the two-position switch with -VIN of the LED driver. Fit the switch at the hole on the top of the 3D printed case. Connect the yellow to +VIN and the blue wire to PWM. Connect the black and red wires of the

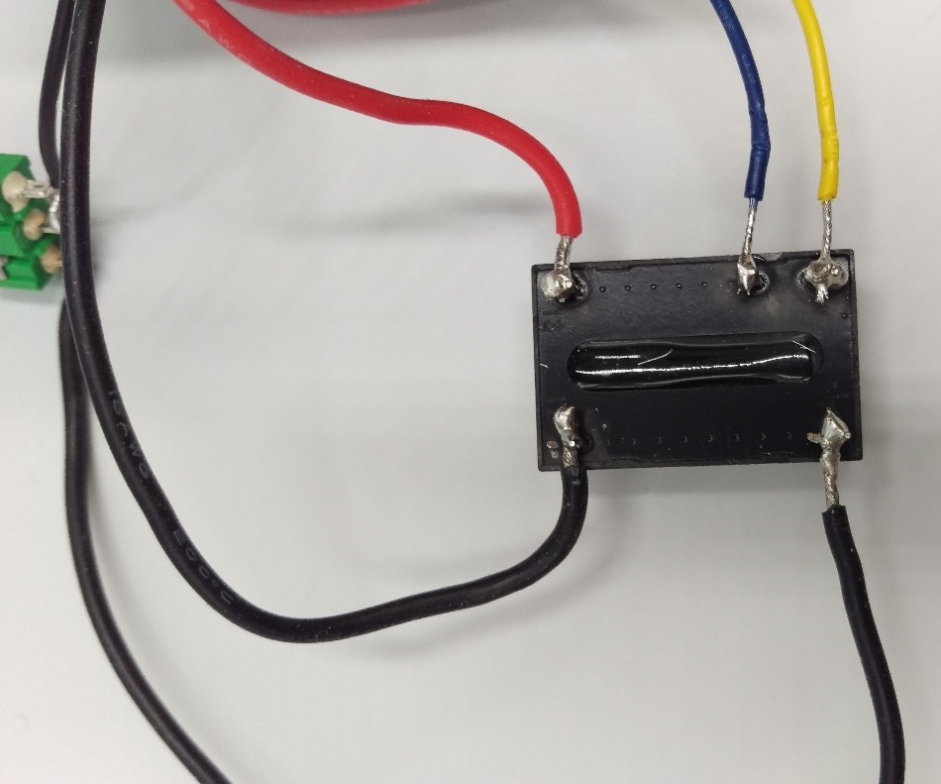
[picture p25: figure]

LED out connectors to -VOUT and +VOUT.

3) Fix the nylon spacers to the LED Driver holder using the nylon nuts. Fix this assembly to the base plate using 4 M3 8 mm screws. Push the LED driver gently into the holder until you feel a resistance.
O +VOUT | O PWM O +VIN
O -VOUT | O -VIN

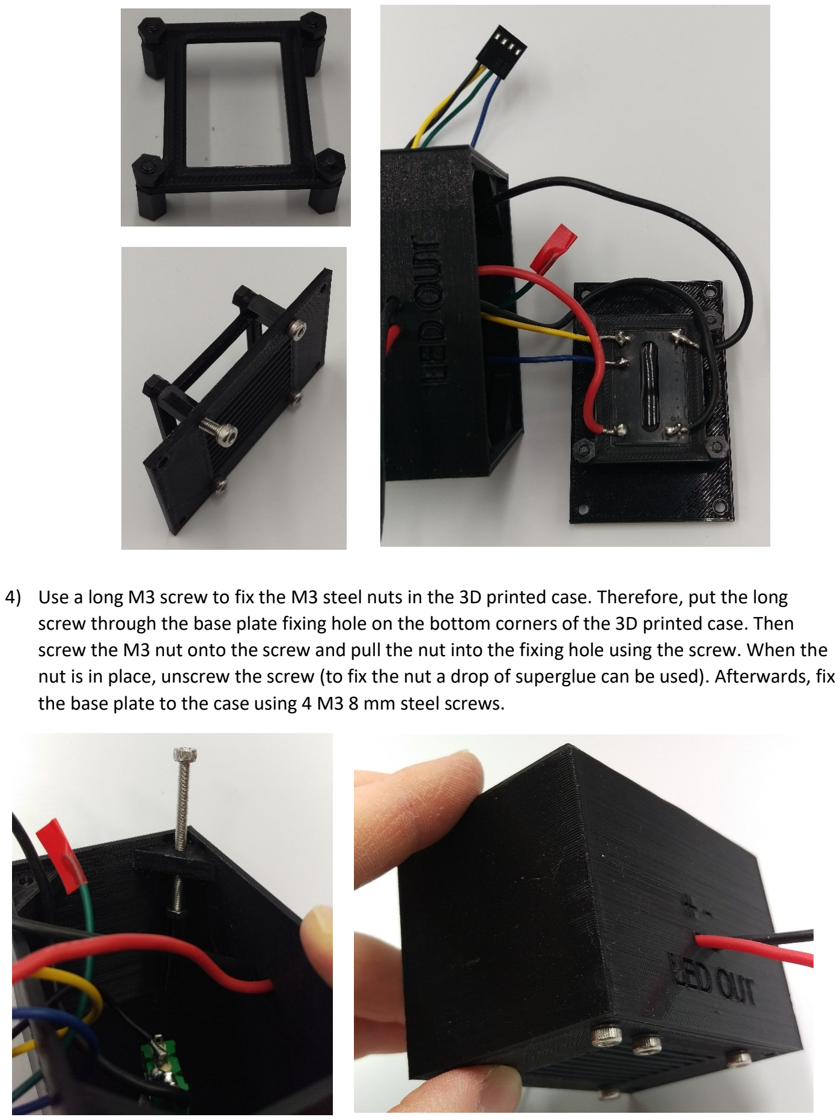
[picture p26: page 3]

4) Use a long M3 screw to fix the M3 steel nuts in the 3D printed case. Therefore, put the long screw through the base plate fixing hole on the bottom corners of the 3D printed case. Then screw the M3 nut onto the screw and pull the nut into the fixing hole using the screw. When the nut is in place, unscrew the screw (to fix the nut a drop of superglue can be used). Afterwards, fix the base plate to the case using 4 M3 8 mm steel screws.

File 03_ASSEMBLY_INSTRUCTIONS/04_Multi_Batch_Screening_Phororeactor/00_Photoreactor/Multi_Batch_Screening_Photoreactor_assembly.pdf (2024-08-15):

setPageBoxes("Crop", 0, 0, [0,2000,2000,0]);

# Assembly Instructions

TITLE

Multi-Batch Screening
Photoreactor

ORGANIZATION

Institute of Chemical
Engineering Ulm University | INSTRUCTIONS DESIGNER | Daniel Kowalczyk
1) placement of the base modules: The base module is clipped to the the corresponding openings of the IKA Roller 10.
2) assembly of the irradiation module: The used SMD mounted LEDs can be fixed to the 300 mm aluminum heat sinks at variable positions in 20 mm steps. The LEDs are mounted at the precut heat sink threads (M3) using 2 M3 (5 mm) screws. The used LEDs are connected in a row, a 1 A fuse is incorporated in front of every module to protect the LEDs from higher currents. The irradiation modules are connected to the power supply using 4 mm banana plugs. The heat sink holder is mounted using 2 M3 (5 mm) screws.
placement of the irradiation module: The irradiation module stand is fixed tor the heat sink holder using 2 M3 (25 mm) screws and corresponding nuts. After the assembly of the irradiation module is finished it can be clipped to the installed base module.
3) assembly of the reflector module: The PTFE side walls are mounted to the reflector holder using 4 M3 (8 mm) screws and corresponding nuts. The PTFE reflector is placed within the guideway of the reflector holder. The two reflector holder parts are connected using 4 M3 (10 mm) screws and corresponding nuts.
placement of the irradiation module: The reflector module is clipped on top of the irradiation modules.

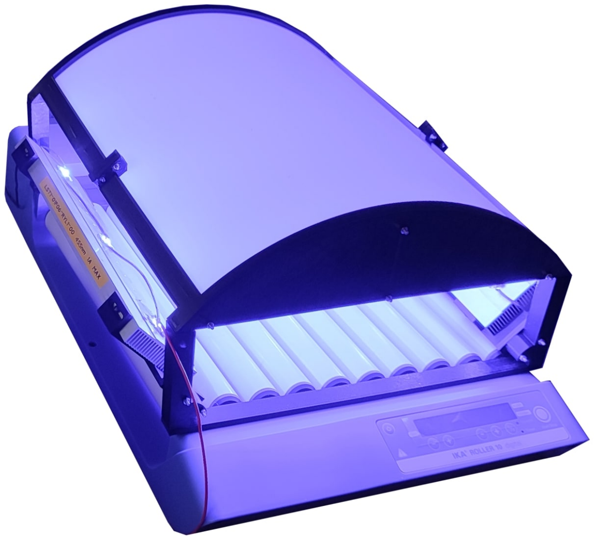
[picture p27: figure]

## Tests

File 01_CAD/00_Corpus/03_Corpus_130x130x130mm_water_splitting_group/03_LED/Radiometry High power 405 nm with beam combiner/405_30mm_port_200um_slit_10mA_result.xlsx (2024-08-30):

Slit / um | Diam. / mm | WL / nm | Spectral / W/nm | Total / mW
200 | 30 | 200.2437506 | 0 | 898.3070374
200 | 30 | 200.8477938 | 0 | 898.3070374
200 | 30 | 201.4518133 | 0 | 898.3070374
200 | 30 | 202.0558091 | 0 | 898.3070374
200 | 30 | 202.6597812 | 0 | 898.3070374
200 | 30 | 203.2637295 | 0 | 898.3070374
200 | 30 | 203.8676541 | 0 | 898.3070374
200 | 30 | 204.4715549 | 0 | 898.3070374
200 | 30 | 205.0754319 | 0 | 898.3070374
200 | 30 | 205.6792851 | 0 | 898.3070374
200 | 30 | 206.2831144 | 0 | 898.3070374
200 | 30 | 206.8869199 | 0 | 898.3070374
200 | 30 | 207.4907016 | 0 | 898.3070374
200 | 30 | 208.0944593 | 0 | 898.3070374
200 | 30 | 208.6981932 | 0 | 898.3070374
200 | 30 | 209.3019031 | 0 | 898.3070374
200 | 30 | 209.9055891 | 0 | 898.3070374
200 | 30 | 210.5092511 | 0 | 898.3070374
200 | 30 | 211.1128891 | 0 | 898.3070374
200 | 30 | 211.7165032 | 0 | 898.3070374
200 | 30 | 212.3200932 | 0 | 898.3070374
200 | 30 | 212.9236592 | 0 | 898.3070374
200 | 30 | 213.5272011 | 0 | 898.3070374
200 | 30 | 214.130719 | 0 | 898.3070374
200 | 30 | 214.7342128 | 0 | 898.3070374
200 | 30 | 215.3376825 | 0 | 898.3070374
200 | 30 | 215.941128 | 0 | 898.3070374
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

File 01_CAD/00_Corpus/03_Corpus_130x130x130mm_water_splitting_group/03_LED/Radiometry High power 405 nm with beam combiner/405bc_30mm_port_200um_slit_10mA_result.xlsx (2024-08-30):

Slit / um | Diam. / mm | WL / nm | Spectral / W/nm | Total / mW
200 | 30 | 200.2437506 | 0 | 488.0299517
200 | 30 | 200.8477938 | 0 | 488.0299517
200 | 30 | 201.4518133 | 0 | 488.0299517
200 | 30 | 202.0558091 | 0 | 488.0299517
200 | 30 | 202.6597812 | 8.837785569e-05 | 488.0299517
200 | 30 | 203.2637295 | 0.0001953241276 | 488.0299517
200 | 30 | 203.8676541 | 2.044014321e-05 | 488.0299517
200 | 30 | 204.4715549 | 0.0001101338776 | 488.0299517
200 | 30 | 205.0754319 | 0.0002473946296 | 488.0299517
200 | 30 | 205.6792851 | 0.0002544399184 | 488.0299517
200 | 30 | 206.2831144 | 0.0001892191263 | 488.0299517
200 | 30 | 206.8869199 | 0 | 488.0299517
200 | 30 | 207.4907016 | 1.368751249e-05 | 488.0299517
200 | 30 | 208.0944593 | 0 | 488.0299517
200 | 30 | 208.6981932 | 1.931532165e-05 | 488.0299517
200 | 30 | 209.3019031 | 3.681520691e-05 | 488.0299517
200 | 30 | 209.9055891 | 0.0003071868828 | 488.0299517
200 | 30 | 210.5092511 | 0 | 488.0299517
200 | 30 | 211.1128891 | 0 | 488.0299517
200 | 30 | 211.7165032 | 0.0003144556146 | 488.0299517
200 | 30 | 212.3200932 | 0 | 488.0299517
200 | 30 | 212.9236592 | 0.0002425659669 | 488.0299517
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

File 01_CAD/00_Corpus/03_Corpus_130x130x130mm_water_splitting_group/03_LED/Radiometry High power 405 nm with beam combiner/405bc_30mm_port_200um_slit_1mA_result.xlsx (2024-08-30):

Slit / um | Diam. / mm | WL / nm | Spectral / W/nm | Total / mW
200 | 30 | 200.2437506 | 2.232786485e-05 | 74.73018743
200 | 30 | 200.8477938 | 0 | 74.73018743
200 | 30 | 201.4518133 | 4.521146636e-05 | 74.73018743
200 | 30 | 202.0558091 | 8.842480449e-06 | 74.73018743
200 | 30 | 202.6597812 | 4.243496442e-05 | 74.73018743
200 | 30 | 203.2637295 | 7.577678915e-05 | 74.73018743
200 | 30 | 203.8676541 | 0 | 74.73018743
200 | 30 | 204.4715549 | 1.77362141e-05 | 74.73018743
200 | 30 | 205.0754319 | 2.770300672e-05 | 74.73018743
200 | 30 | 205.6792851 | 4.374719786e-05 | 74.73018743
200 | 30 | 206.2831144 | 3.819179714e-05 | 74.73018743
200 | 30 | 206.8869199 | 3.687790455e-05 | 74.73018743
200 | 30 | 207.4907016 | 2.209765975e-05 | 74.73018743
200 | 30 | 208.0944593 | 0 | 74.73018743
200 | 30 | 208.6981932 | 2.268739898e-05 | 74.73018743
200 | 30 | 209.3019031 | 3.413521055e-05 | 74.73018743
200 | 30 | 209.9055891 | 4.430566261e-05 | 74.73018743
200 | 30 | 210.5092511 | 1.452861486e-05 | 74.73018743
200 | 30 | 211.1128891 | 2.716756988e-05 | 74.73018743
200 | 30 | 211.7165032 | 8.797222247e-05 | 74.73018743
200 | 30 | 212.3200932 | 3.065213348e-05 | 74.73018743
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

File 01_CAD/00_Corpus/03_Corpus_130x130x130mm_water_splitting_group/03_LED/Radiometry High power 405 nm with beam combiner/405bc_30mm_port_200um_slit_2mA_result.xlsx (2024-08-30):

Slit / um | Diam. / mm | WL / nm | Spectral / W/nm | Total / mW
200 | 30 | 200.2437506 | 0 | 150.5268664
200 | 30 | 200.8477938 | 0 | 150.5268664
200 | 30 | 201.4518133 | 0 | 150.5268664
200 | 30 | 202.0558091 | 0 | 150.5268664
200 | 30 | 202.6597812 | 1.354376061e-05 | 150.5268664
200 | 30 | 203.2637295 | 4.657555481e-05 | 150.5268664
200 | 30 | 203.8676541 | 0 | 150.5268664
200 | 30 | 204.4715549 | 0 | 150.5268664
200 | 30 | 205.0754319 | 5.570928037e-05 | 150.5268664
200 | 30 | 205.6792851 | 0 | 150.5268664
200 | 30 | 206.2831144 | 4.298215031e-05 | 150.5268664
200 | 30 | 206.8869199 | 3.46582193e-05 | 150.5268664
200 | 30 | 207.4907016 | 0 | 150.5268664
200 | 30 | 208.0944593 | 0 | 150.5268664
200 | 30 | 208.6981932 | 0 | 150.5268664
200 | 30 | 209.3019031 | 0 | 150.5268664
200 | 30 | 209.9055891 | 5.558364761e-05 | 150.5268664
200 | 30 | 210.5092511 | 0 | 150.5268664
200 | 30 | 211.1128891 | 0 | 150.5268664
200 | 30 | 211.7165032 | 0 | 150.5268664
200 | 30 | 212.3200932 | 0 | 150.5268664
200 | 30 | 212.9236592 | 0 | 150.5268664
200 | 30 | 213.5272011 | 0 | 150.5268664
200 | 30 | 214.130719 | 8.805982697e-06 | 150.5268664
200 | 30 | 214.7342128 | 8.803676162e-07 | 150.5268664
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

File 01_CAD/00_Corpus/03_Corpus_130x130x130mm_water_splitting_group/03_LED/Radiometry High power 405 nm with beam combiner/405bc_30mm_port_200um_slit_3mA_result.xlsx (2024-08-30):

Slit / um | Diam. / mm | WL / nm | Spectral / W/nm | Total / mW
200 | 30 | 200.2437506 | 0 | 219.8397396
200 | 30 | 200.8477938 | 0 | 219.8397396
200 | 30 | 201.4518133 | 0 | 219.8397396
200 | 30 | 202.0558091 | 0 | 219.8397396
200 | 30 | 202.6597812 | 2.351913197e-05 | 219.8397396
200 | 30 | 203.2637295 | 0 | 219.8397396
200 | 30 | 203.8676541 | 0 | 219.8397396
200 | 30 | 204.4715549 | 0 | 219.8397396
200 | 30 | 205.0754319 | 0 | 219.8397396
200 | 30 | 205.6792851 | 4.833984036e-05 | 219.8397396
200 | 30 | 206.2831144 | 5.251057945e-05 | 219.8397396
200 | 30 | 206.8869199 | 0 | 219.8397396
200 | 30 | 207.4907016 | 6.381522762e-05 | 219.8397396
200 | 30 | 208.0944593 | 0 | 219.8397396
200 | 30 | 208.6981932 | 5.738904131e-05 | 219.8397396
200 | 30 | 209.3019031 | 0 | 219.8397396
200 | 30 | 209.9055891 | 0 | 219.8397396
200 | 30 | 210.5092511 | 0 | 219.8397396
200 | 30 | 211.1128891 | 0 | 219.8397396
200 | 30 | 211.7165032 | 0.0001151390829 | 219.8397396
200 | 30 | 212.3200932 | 3.839857051e-05 | 219.8397396
200 | 30 | 212.9236592 | 1.258293627e-05 | 219.8397396
200 | 30 | 213.5272011 | 2.317622609e-05 | 219.8397396
200 | 30 | 214.130719 | 0 | 219.8397396
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

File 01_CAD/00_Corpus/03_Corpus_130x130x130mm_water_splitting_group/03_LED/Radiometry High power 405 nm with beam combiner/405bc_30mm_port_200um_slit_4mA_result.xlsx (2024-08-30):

Slit / um | Diam. / mm | WL / nm | Spectral / W/nm | Total / mW
200 | 30 | 200.2437506 | 9.557498511e-05 | 285.3492671
200 | 30 | 200.8477938 | 0 | 285.3492671
200 | 30 | 201.4518133 | 1.068685911e-05 | 285.3492671
200 | 30 | 202.0558091 | 0 | 285.3492671
200 | 30 | 202.6597812 | 8.85466366e-05 | 285.3492671
200 | 30 | 203.2637295 | 0.0002796866893 | 285.3492671
200 | 30 | 203.8676541 | 6.969763717e-05 | 285.3492671
200 | 30 | 204.4715549 | 0 | 285.3492671
200 | 30 | 205.0754319 | 0.0001674925583 | 285.3492671
200 | 30 | 205.6792851 | 0.0001678598397 | 285.3492671
200 | 30 | 206.2831144 | 0.0001054626202 | 285.3492671
200 | 30 | 206.8869199 | 4.699222253e-05 | 285.3492671
200 | 30 | 207.4907016 | 7.144359306e-05 | 285.3492671
200 | 30 | 208.0944593 | 0 | 285.3492671
200 | 30 | 208.6981932 | 0 | 285.3492671
200 | 30 | 209.3019031 | 7.158874654e-05 | 285.3492671
200 | 30 | 209.9055891 | 4.177223337e-05 | 285.3492671
200 | 30 | 210.5092511 | 0 | 285.3492671
200 | 30 | 211.1128891 | 0 | 285.3492671
200 | 30 | 211.7165032 | 0.0002946947943 | 285.3492671
200 | 30 | 212.3200932 | 0.0001728500528 | 285.3492671
200 | 30 | 212.9236592 | 0.0002428145562 | 285.3492671
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

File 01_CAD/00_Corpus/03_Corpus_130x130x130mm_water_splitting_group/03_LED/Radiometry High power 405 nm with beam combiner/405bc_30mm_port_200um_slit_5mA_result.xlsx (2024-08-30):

Slit / um | Diam. / mm | WL / nm | Spectral / W/nm | Total / mW
200 | 30 | 200.2437506 | 9.952519863e-05 | 339.5925755
200 | 30 | 200.8477938 | 3.57968781e-05 | 339.5925755
200 | 30 | 201.4518133 | 0 | 339.5925755
200 | 30 | 202.0558091 | 0 | 339.5925755
200 | 30 | 202.6597812 | 9.116499828e-06 | 339.5925755
200 | 30 | 203.2637295 | 4.926566591e-05 | 339.5925755
200 | 30 | 203.8676541 | 0 | 339.5925755
200 | 30 | 204.4715549 | 0 | 339.5925755
200 | 30 | 205.0754319 | 0.000195515891 | 339.5925755
200 | 30 | 205.6792851 | 0.0002350011189 | 339.5925755
200 | 30 | 206.2831144 | 0.0001299589811 | 339.5925755
200 | 30 | 206.8869199 | 0 | 339.5925755
200 | 30 | 207.4907016 | 0 | 339.5925755
200 | 30 | 208.0944593 | 0 | 339.5925755
200 | 30 | 208.6981932 | 5.588758521e-05 | 339.5925755
200 | 30 | 209.3019031 | 5.683986023e-05 | 339.5925755
200 | 30 | 209.9055891 | 4.433531341e-05 | 339.5925755
200 | 30 | 210.5092511 | 0 | 339.5925755
200 | 30 | 211.1128891 | 3.126095445e-06 | 339.5925755
200 | 30 | 211.7165032 | 0.0002046224273 | 339.5925755
200 | 30 | 212.3200932 | 0 | 339.5925755
200 | 30 | 212.9236592 | 8.792735577e-05 | 339.5925755
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

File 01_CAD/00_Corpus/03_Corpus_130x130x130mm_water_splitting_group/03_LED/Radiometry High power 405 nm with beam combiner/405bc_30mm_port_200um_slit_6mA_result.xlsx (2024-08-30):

Slit / um | Diam. / mm | WL / nm | Spectral / W/nm | Total / mW
200 | 30 | 200.2437506 | 3.085990627e-05 | 387.0969161
200 | 30 | 200.8477938 | 4.158599898e-05 | 387.0969161
200 | 30 | 201.4518133 | 0 | 387.0969161
200 | 30 | 202.0558091 | 0 | 387.0969161
200 | 30 | 202.6597812 | 0 | 387.0969161
200 | 30 | 203.2637295 | 0.0002333883781 | 387.0969161
200 | 30 | 203.8676541 | 0 | 387.0969161
200 | 30 | 204.4715549 | 5.78643172e-05 | 387.0969161
200 | 30 | 205.0754319 | 0.0001588710704 | 387.0969161
200 | 30 | 205.6792851 | 0.0002010752245 | 387.0969161
200 | 30 | 206.2831144 | 0.000174652408 | 387.0969161
200 | 30 | 206.8869199 | 0.0001215645815 | 387.0969161
200 | 30 | 207.4907016 | 0.000177218904 | 387.0969161
200 | 30 | 208.0944593 | 0 | 387.0969161
200 | 30 | 208.6981932 | 9.326530905e-05 | 387.0969161
200 | 30 | 209.3019031 | 4.203711302e-06 | 387.0969161
200 | 30 | 209.9055891 | 0.0002150502893 | 387.0969161
200 | 30 | 210.5092511 | 0 | 387.0969161
200 | 30 | 211.1128891 | 0 | 387.0969161
200 | 30 | 211.7165032 | 0.0002015222086 | 387.0969161
200 | 30 | 212.3200932 | 0.0001584049784 | 387.0969161
200 | 30 | 212.9236592 | 6.681933386e-05 | 387.0969161
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

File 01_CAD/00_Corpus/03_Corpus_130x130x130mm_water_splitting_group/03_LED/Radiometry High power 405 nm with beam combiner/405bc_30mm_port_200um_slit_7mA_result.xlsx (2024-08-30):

Slit / um | Diam. / mm | WL / nm | Spectral / W/nm | Total / mW
200 | 30 | 200.2437506 | 0 | 422.1315359
200 | 30 | 200.8477938 | 0 | 422.1315359
200 | 30 | 201.4518133 | 0 | 422.1315359
200 | 30 | 202.0558091 | 0 | 422.1315359
200 | 30 | 202.6597812 | 8.548145616e-05 | 422.1315359
200 | 30 | 203.2637295 | 0.0002320706962 | 422.1315359
200 | 30 | 203.8676541 | 0 | 422.1315359
200 | 30 | 204.4715549 | 5.147814458e-05 | 422.1315359
200 | 30 | 205.0754319 | 0.0002266245589 | 422.1315359
200 | 30 | 205.6792851 | 0.0003404653843 | 422.1315359
200 | 30 | 206.2831144 | 0.0001355071607 | 422.1315359
200 | 30 | 206.8869199 | 1.84974797e-06 | 422.1315359
200 | 30 | 207.4907016 | 0.0001041033358 | 422.1315359
200 | 30 | 208.0944593 | 0 | 422.1315359
200 | 30 | 208.6981932 | 0 | 422.1315359
200 | 30 | 209.3019031 | 9.812215824e-05 | 422.1315359
200 | 30 | 209.9055891 | 0.0001696070955 | 422.1315359
200 | 30 | 210.5092511 | 0 | 422.1315359
200 | 30 | 211.1128891 | 0 | 422.1315359
200 | 30 | 211.7165032 | 0.0001789019777 | 422.1315359
200 | 30 | 212.3200932 | 0.0001235417224 | 422.1315359
200 | 30 | 212.9236592 | 0.0001568470741 | 422.1315359
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

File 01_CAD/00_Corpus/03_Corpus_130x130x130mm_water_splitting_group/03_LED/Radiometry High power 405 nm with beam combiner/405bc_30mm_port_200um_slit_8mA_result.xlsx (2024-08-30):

Slit / um | Diam. / mm | WL / nm | Spectral / W/nm | Total / mW
200 | 30 | 200.2437506 | 0 | 455.2709165
200 | 30 | 200.8477938 | 0 | 455.2709165
200 | 30 | 201.4518133 | 5.567104683e-05 | 455.2709165
200 | 30 | 202.0558091 | 0 | 455.2709165
200 | 30 | 202.6597812 | 5.222285389e-06 | 455.2709165
200 | 30 | 203.2637295 | 0.0002475949812 | 455.2709165
200 | 30 | 203.8676541 | 0.0001186205737 | 455.2709165
200 | 30 | 204.4715549 | 0.0001946103014 | 455.2709165
200 | 30 | 205.0754319 | 0.0002753212438 | 455.2709165
200 | 30 | 205.6792851 | 0.0001471947949 | 455.2709165
200 | 30 | 206.2831144 | 0.000109834781 | 455.2709165
200 | 30 | 206.8869199 | 8.500253948e-05 | 455.2709165
200 | 30 | 207.4907016 | 2.61328454e-05 | 455.2709165
200 | 30 | 208.0944593 | 0 | 455.2709165
200 | 30 | 208.6981932 | 0 | 455.2709165
200 | 30 | 209.3019031 | 0.0002475568933 | 455.2709165
200 | 30 | 209.9055891 | 8.84837504e-05 | 455.2709165
200 | 30 | 210.5092511 | 0 | 455.2709165
200 | 30 | 211.1128891 | 0 | 455.2709165
200 | 30 | 211.7165032 | 0.0001398393937 | 455.2709165
200 | 30 | 212.3200932 | 7.177017388e-05 | 455.2709165
200 | 30 | 212.9236592 | 9.019436126e-05 | 455.2709165
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

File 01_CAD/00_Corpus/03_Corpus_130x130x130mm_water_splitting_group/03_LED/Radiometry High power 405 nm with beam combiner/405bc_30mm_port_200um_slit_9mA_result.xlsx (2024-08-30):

Slit / um | Diam. / mm | WL / nm | Spectral / W/nm | Total / mW
200 | 30 | 200.2437506 | 0 | 473.5951741
200 | 30 | 200.8477938 | 0 | 473.5951741
200 | 30 | 201.4518133 | 0 | 473.5951741
200 | 30 | 202.0558091 | 0 | 473.5951741
200 | 30 | 202.6597812 | 0 | 473.5951741
200 | 30 | 203.2637295 | 9.121063744e-05 | 473.5951741
200 | 30 | 203.8676541 | 0 | 473.5951741
200 | 30 | 204.4715549 | 0 | 473.5951741
200 | 30 | 205.0754319 | 0.0001347299096 | 473.5951741
200 | 30 | 205.6792851 | 0.0001604747275 | 473.5951741
200 | 30 | 206.2831144 | 6.90326053e-05 | 473.5951741
200 | 30 | 206.8869199 | 3.234451537e-05 | 473.5951741
200 | 30 | 207.4907016 | 0 | 473.5951741
200 | 30 | 208.0944593 | 0 | 473.5951741
200 | 30 | 208.6981932 | 8.679100345e-05 | 473.5951741
200 | 30 | 209.3019031 | 3.527482234e-05 | 473.5951741
200 | 30 | 209.9055891 | 1.594326709e-05 | 473.5951741
200 | 30 | 210.5092511 | 0 | 473.5951741
200 | 30 | 211.1128891 | 0 | 473.5951741
200 | 30 | 211.7165032 | 0.0001486716603 | 473.5951741
200 | 30 | 212.3200932 | 0.0002480370594 | 473.5951741
200 | 30 | 212.9236592 | 0.0002490877333 | 473.5951741
200 | 30 | 213.5272011 | 4.77834108e-05 | 473.5951741
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

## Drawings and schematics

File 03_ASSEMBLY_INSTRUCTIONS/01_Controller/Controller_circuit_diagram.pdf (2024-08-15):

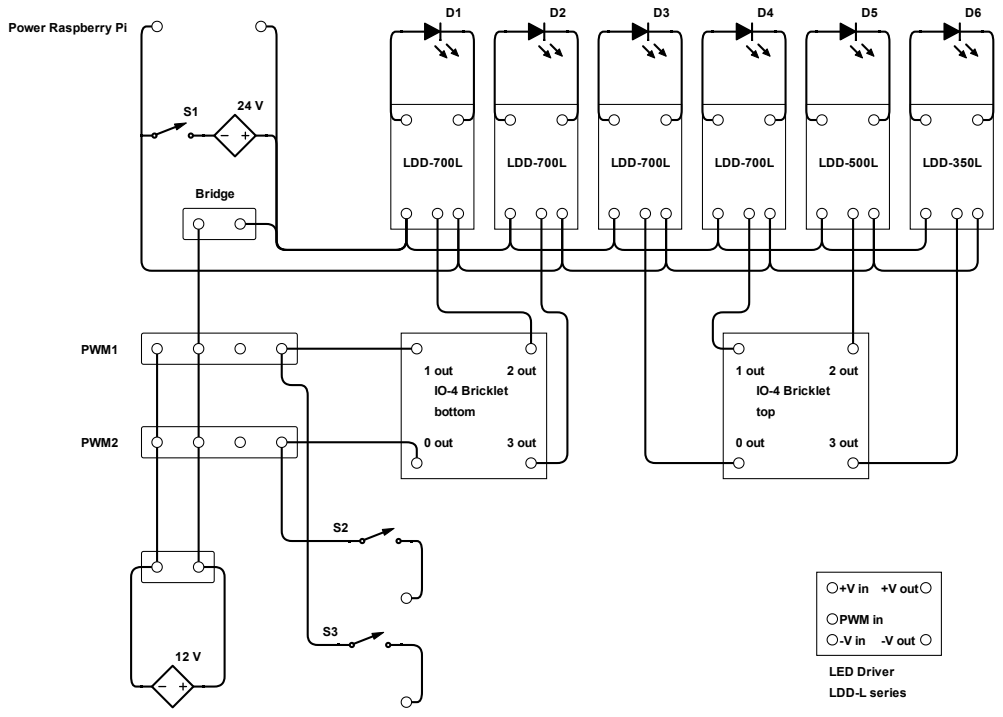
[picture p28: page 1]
LDD-700L; LDD-500L; LDD-350L; IO-4 Bricklet top; IO-4 Bricklet; 0 out; 1 out; 2 out; 3 out; bottom; PWM in; +V out; -V out; LDD-L series; LED Driver; Bridge; PWM1; PWM2

Power Raspberry Pi

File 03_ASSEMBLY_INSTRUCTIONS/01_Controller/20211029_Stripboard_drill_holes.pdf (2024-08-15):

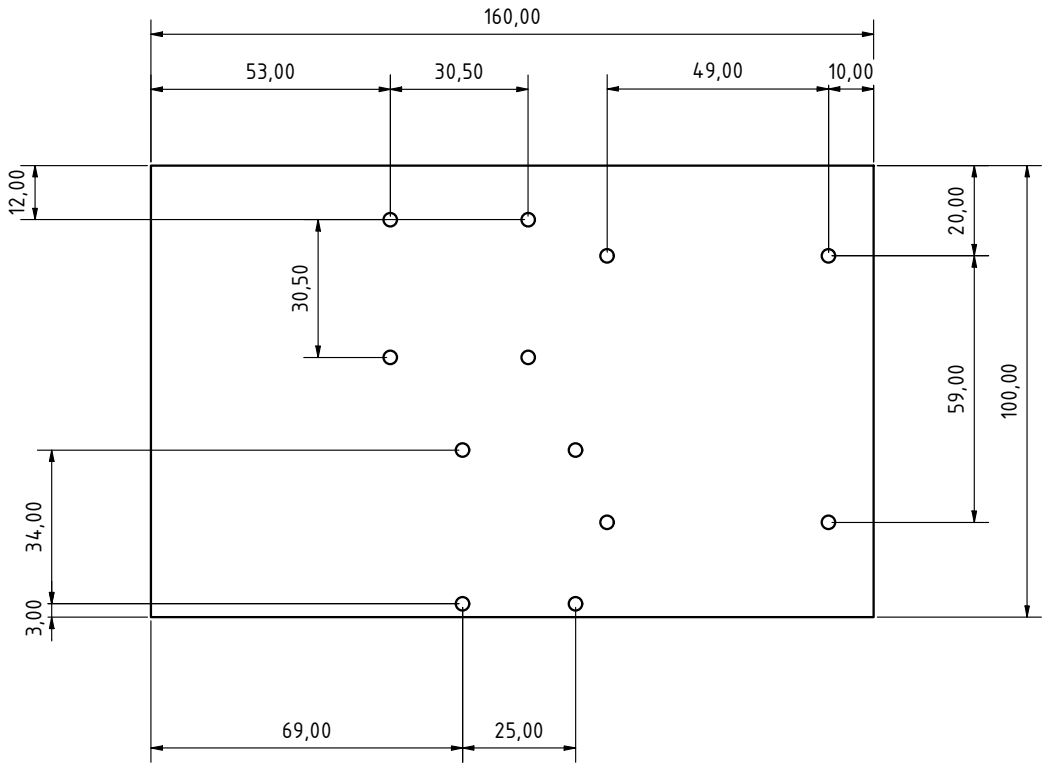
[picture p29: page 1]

Datum | Name

Gezeich | 29.10.2021 | Daniel

Kontroll

Norm

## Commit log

2024-08-15 add repo
    [20210104_Thorlabsl_modul.stl, 300mm_alu_heatsink.stl, Base_Module.stl, PTFE_Side_Wall.stl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]
2024-08-16 Update Readme.md
    add korad power supply info file
2024-08-16 add corpus_90x90x140mm_side_walls_LED_Irradiation_Firesting_ports .ipt, .stl and .yaml files
    [corpus_90x90x140mm_side_walls_LED_Irradiation_Firesting_ports.ipt, corpus_90x90x140mm_side_walls_LED_Irradiation_Firesting_ports.stl]
2024-08-30 Addition of left and right wall with accessories for the Corpus_130X130X130mm_water_splitting group
    [2021_03_30_Stabilisator_Korpus.ipt, 2021_03_30_Stabilisator_Korpus.stl, 2024_08_20_dummy_aperture.ipt, 2024_08_20_dummy_aperture.stl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]
2025-01-14 Finish of documentation of adavneced irradiation setup V1.0
    [20210330_5mmFuss_Korpus.ipt, 2024_08_21_Reaktorkorpus_modular_hinten.stl, 2024_08_26_Double_walled_beaker_recess_2,1cm.ipt, 2024_08_26_Double_walled_beaker_rec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]
2025-11-19 Addition of power measuremnt setup for water splitting group reactor and addition if aperture for UHP LEDs when used with beam combiner
    [20210330_5mmFuss_Korpus.ipt, 2021_03_30_Stabilisator_Korpus.ipt, 2021_03_30_Stabilisator_Korpus.stl, 2024_08_20_dummy_aperture.ipt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]
